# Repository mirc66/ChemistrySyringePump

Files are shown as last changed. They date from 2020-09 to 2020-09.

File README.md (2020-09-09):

# ChemistrySyringePump
arduino based 300ml syringe pump  with LED display and control buttons

Not included stepper motor or rail description

old LCD Key board Sparkfun produce 13293 now obsolete.
New LCD Key board Adafruit product 772
Uses BigEasyDriver board for stepper motor control  from Sparkfun part 12859

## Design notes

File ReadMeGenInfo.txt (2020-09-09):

ReadMe
1. final syringe pump program old board multiple selectable speeds in mL/min:syringePump300mL_revisedV2
2. final syringe pump program old board single spleed 50ml/min:syringePump300mLvs3
3. final syringe pump program New board multiple selectable speeds in mL/min:syringePump300mL_revised_NewBoardMR4_3

Orig programs received from Hans and Rob

older program:
  	SyringePump300ml.ino  
  	opening menu that says: Syringe pump v2.0
	has hardcoded single speed using the SPEED_MICROSECOND_DELAY  variable  
		SPEED_MICROSECOND_DELAY : 	a)30   for 400 mL/min ????
						b)450  for 50 mL/min
						c)2250 for 10 mL/min

Newer program:
	SyringePump300ml_revised.ino
	opening menu that says: Syringe pump
	adds variable speed control

Note:
 the pump i got from  Alex had  the old program running on it.  
Rob said the New Program should run on the old hardware

To send prog to arduino coonect straight to usb on computer not trough multi usb hub

Stepper Motor:
++++++++++++++++++++++++++++++++++++++++++++++++++++++++++++++++++++++++++++++++++++++++++++
sample code: http://www.schmalzhaus.com/EasyDriver/Examples/EasyDriverExamples.html

void setup() {                
  pinMode(8, OUTPUT);
  pinMode(9, OUTPUT);
  digitalWrite(8, LOW);
  digitalWrite(9, LOW);
}el

void loop() {
  digitalWrite(9, HIGH);
  delay(1);          
  digitalWrite(9, LOW); 
  delay(1);          
}
++++++++++++++++++++++++++++++++++++++++++++++++++++++++++++++++++++++

1.8deg/step so 200 full steps per revolution.  Big Easy Diver board defaults to 16 microsteps so total of 3200 microStep per revolution

Motor Speed:
delay() in ms since the code above uses 1ms High and 1 ms Low you each microstep takes 2ms
delayMicroseconds() in microSec eg 10microSec h ad 10 microSec low  takes 20 microSec per microStep

delay(1):	microStep/2ms*1000ms/sec = 500microStep/sec

delay(10):	microStep/20ms*1000ms/sec= 50microStep/sec

delayMicrosec(50):	microStep/100microsec*1000microsec/msec*1000msec/sec= 10,000microstep/sec

Speed:
syringe vol=300mL
syringe Barrel lenght=155mm
Thread Pitch=1.25mm  this means each ful 360 deg rev the rod avances 1.25mm
Big Easy Driver board defaults to 16 microsteps so full 360 deg rev =200step/rev*16microStep/step=3200 microstep per rev

=
300ml/155mm*1.25mm/rev*rev/3200microstep=0.000756 ml/microStep

syringeVol/syringbarrelLenght *ThredPitch/rev*rev/3200microstep= ml/microStepcalc

flow rate wanted

dealyMicrosec(50):		0.000756ml/microStep*10,000microstep/sec*60sec/min= 453 ml/min fo 50 microsec Delay
see spreadsheet Flowrate calculation syringe pump 2020	

+++++++++++++++++++++++++++++++++++++++++++++++++++++++++++++++++++++++++++++++++++++++++++++

TRIGGERING EXAMPLES:

int triggerPin=9; //not actually connected just a way to create a trigger
pinMode(triggerPin, Input);

Void set up(){}

Void Loop(){
	digitalWrite(triggePin, HIGH);
	//  other code
	if(digitalRead(triggerPin)==HIGH); {
		//do this code so the trigger Pin triggered this code
	}// end if loop
	//otherwise do this
	}//end void loop

+++++++++++++++++++++++++++++++++++++++++++++++++++++++++++++++++++++++++++++++++++++++++++++++++++
Function that returns values rather than a void function that does not return anything

Example:
int myMultiplyFunction(int x, int y){  // returns and integer(int); name of function: myMultiplyFunction; values passed: int x, int y
  int result;
  result = x * y;
  return result;// result is an integer returned to code that called the function
}

++++++++++++++++++++++++++++++++++++++++++++++++++++++++++++++++++++++++++++++++++++++++++++++

User defined Functions created in this program:
Funtion Name			void or parameter to pass
1. ckTrigger()			void
2.readSerial()			void
3.processSerial()		void
4.bolus(Direction)		pass direction( PUSH or PULL)
5.readKey()			void
6.doKeyAction(key)		Pass key
7.updateScreen()		void
8.getKey(input)			pass input
9.decToString(decNumber)	pass decNumber

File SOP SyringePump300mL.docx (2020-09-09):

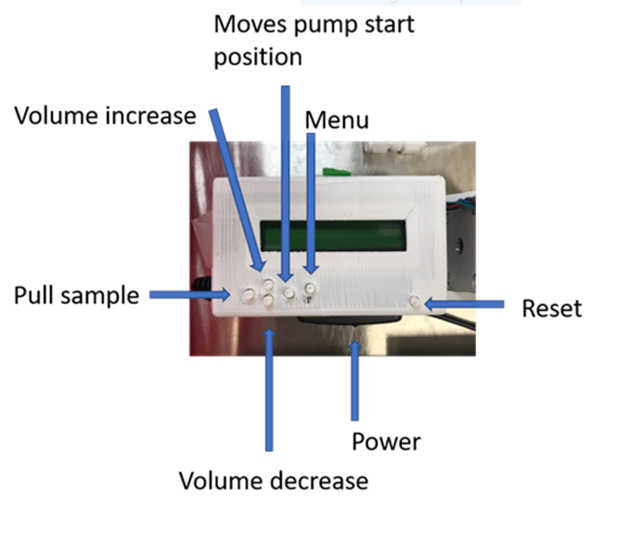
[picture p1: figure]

A-OldBoard hard coded speed of 50 mL/min

Screen at power up for older program SyringePump200mL.ino

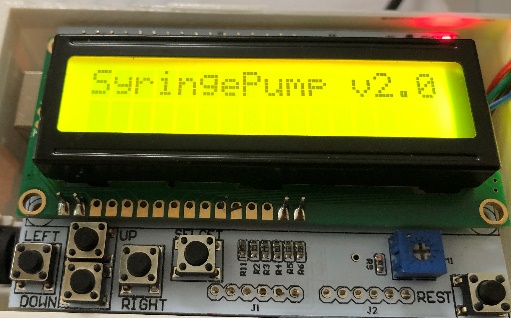
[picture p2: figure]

            1. First Time pressing Select/Menu button: This is the BolusStep Menu

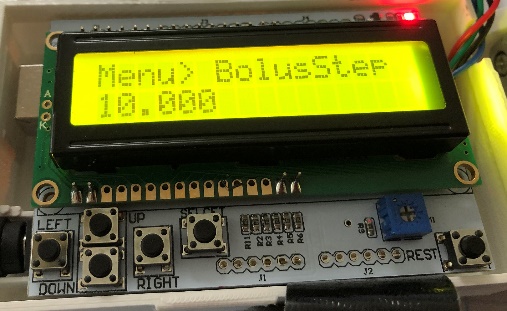
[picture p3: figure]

1. Left and right do nothing on this menu but UP or Down cycle through BolusStep options here did the down button once.

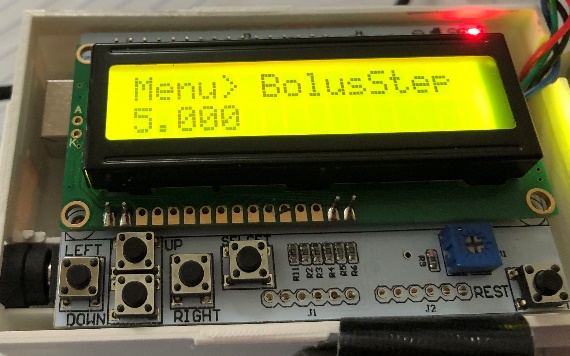
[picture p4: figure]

3.Second time push Select/Menu Button:

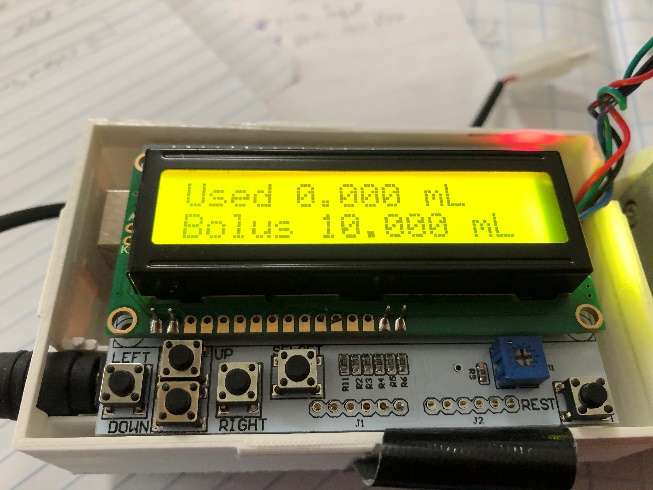
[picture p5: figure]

4. In above menu screen Left (Pull), Right (Push) from the above screen.

5.In above Menu you can change the total Bolus to sample by using up or down buttons on this screen

6. Note Used at the top of the screen will only update if used in push mode if you are pulling it remains 0.000

Old Key Pad Board can select 10 mL/min, 50mL/min or 400mL/min speeds

Open Screen Display:

1. Syringe Pump V2.0 Rob’s original code with extraneous code, old board speed =50 mL/min
2. SyringePumpV3 MR: finalized 7/14/2020 at 10:11am Maritza Romero

Same execution as v2.0 with Hard coded speed currently at 50mL/min (old board)

Old Board removed all sections of code (like triggers and Serial) that did nothing and commented code. Program hard coded speed of syringe in line below.

#define SPEED_MICROSECONDS_DELAY 450 // (450 = 50mL/min for 300mL syringe)

If you want to slow down to 10mL/min change 450 to 2250 on the above line of code

3. SyringePump (old board with selectable syringe speed included extraneous code and errors)
4. SyringePumpV4 still using old board removed extraneous code and corrected errors allows selection of syring speed onscreen

Opening screen V 4 Syringe Pump:

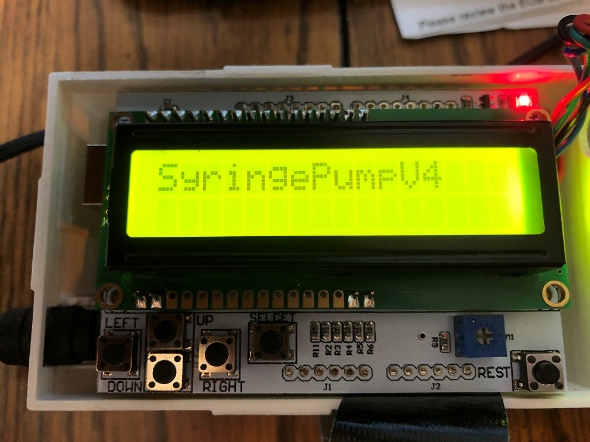
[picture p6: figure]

1. First time press menu key

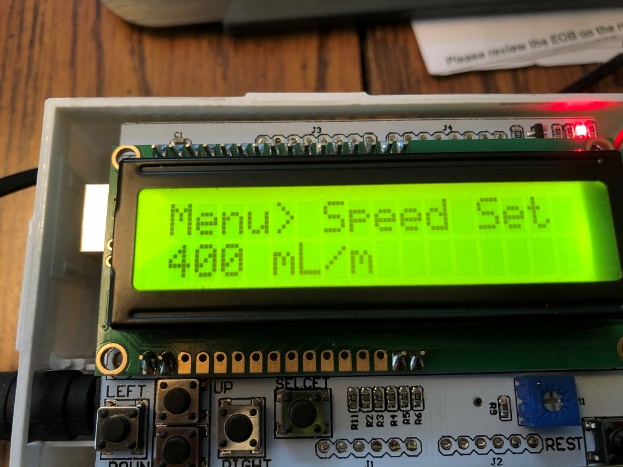
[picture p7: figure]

2. Up or down to select speed you want to use

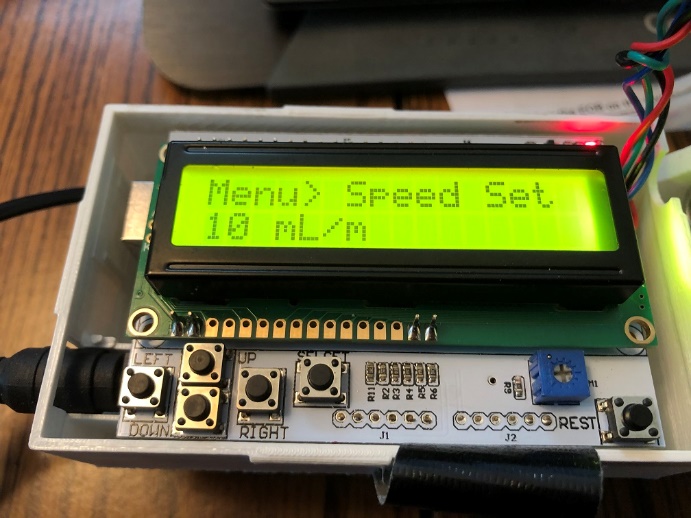
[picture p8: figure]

3. Once speed selected press the Menu button again

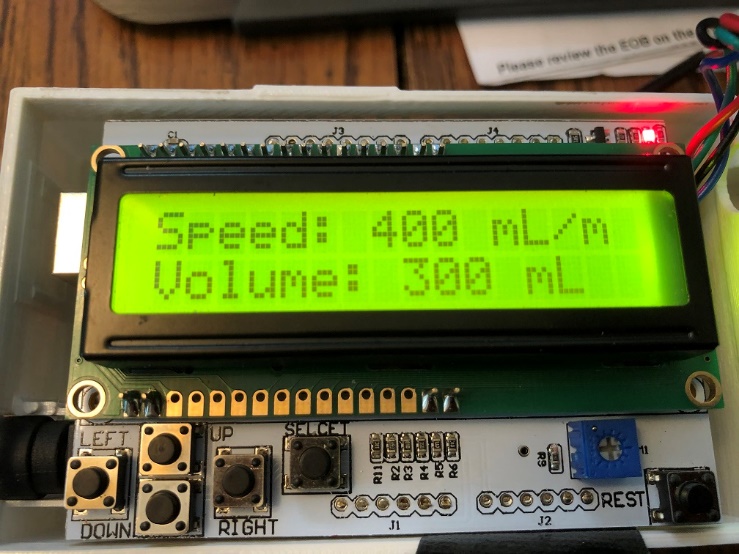
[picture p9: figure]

4. Up and down to change the volume you want to push or sample

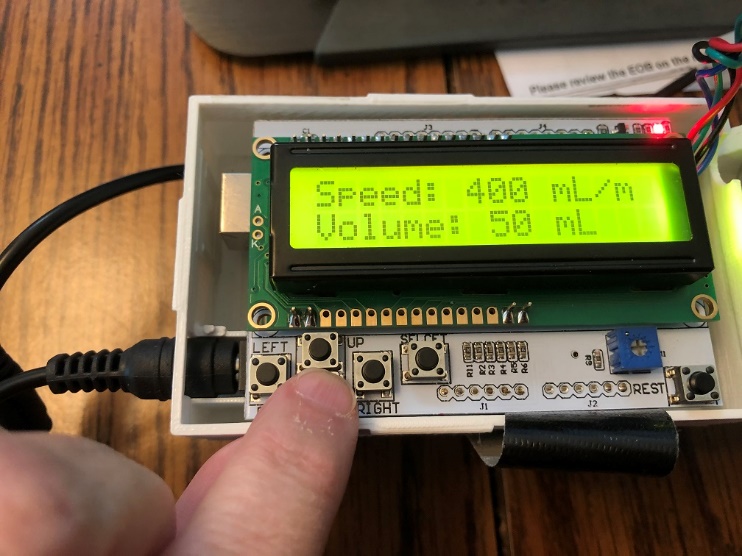
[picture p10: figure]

5. From the above screen push left to pull sample or right to push a volume

New Board : https://www.adafruit.com/product/772

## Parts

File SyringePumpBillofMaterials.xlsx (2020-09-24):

 | Part Name | Vendor | Part #: | unit | quantity | link | price with as of 9/24/2020
1 | 10Series, 1"x2"x24" Aluminum Extrusion | Amazon |  | T-slotted Extrusion | 1 | https://www.amazon.com/80-20-T-Slotted-Extrusion-Black/dp/B00IXOB7AM?s=industrial | $22.23
2 | 25PK-10 Series,Button Head Socket Cap Screw with Slide-In Standard T-Nut | Amazon |  | Screw with T nut | 1 | https://www.amazon.com/dp/B00TE30LUI/?coliid=ASIN-B00TE30LUI-ATVPDKIKX0DER&colid=2DOIGN4AECUGG | $20.89
3 | 16x2 LCD -keyboard shield | adafruit | 772 |  | 1 | https://www.adafruit.com/product/772 | $20.00
4 | arduino Uno R3 (7 to 12V with Max 20V) | Amazon |  | controller | 1 | https://www.amazon.com/dp/B008GRTSV6/?coliid=ASIN-B008GRTSV6-ATVPDKIKX0DER&colid=2DOIGN4AECUGG&psc=1 | $21.00
5 | BigEasyDriver board | sparkfun | ROB-12859 | motor driver | 1 | https://www.sparkfun.com/products/12859 | $20.00
6 | stepper motor | adafruit | 324 | stepper motor | 1 | https://www.adafruit.com/product/324 | $14.00
7 | 5 to 8 mm aluminum flex shaft | adafruit | 1176 | motor to thred rod connector | 1 | https://www.adafruit.com/product/1176 | $5.00
8 | on off switch | adafruit | 1125 | swith with barrel jacks | 1 | https://www.adafruit.com/product/1125 | $3.00
9 | Tenergy 12V 2000mAh rechargeable battery | amazon |  | rechargeable 12V battery | 1 | https://www.amazon.com/Tenergy-Capacity-Rechargeable-Replacement-Equipments/dp/B077Y9HNTF?s=electronics | $23.00
10 | Tenergy battery charger | Amazon |  | 6 to 12V recharger | 1 | https://www.amazon.com/dp/B003MXMJX8/?coliid=ASIN-B003MXMJX8-ATVPDKIKX0DER&colid=2DOIGN4AECUGG&psc=1 | $21.00
12 | connectors battery to connect to charger | amazon |  | VenomTamiya connector set | 1 | https://www.amazon.com/Tamiya-Battery-Device-150mm-Venom/dp/B000HKEVH6 | $6.00
13 | arduino to usb cable | Amazon |  | USB data sync cable arduino | 1 | https://www.amazon.com/Data-Sync-Cable-Arduino-Microcontroller/dp/B01N9IP8LF?s=electronics | $14.00
14 | 316SS- M8-1.25mm threaded rod | McMasterCarr | 94185A160 | 1 meter long | 1 | https://www.mcmaster.com/94185A160/ | $17.00
15 | Linear motion shaft | McMasterCarr | 6112K45 | Carbon Steel, 8 mm Diameter, 400 mm L | 1 | https://www.mcmaster.com/6112K45/ | $15.00
16 | Fixed alignment linear bearing | McMasterCarr | 61205K75 | for 8mm shaft | 1 | https://www.mcmaster.com/61205K75 | $20.00
17 | M3 8mm L pan head SS screws | Amazon |  |  | 1 | https://www.amazon.com/uxcell-Stainless-Steel-Phillips-Screws/dp/B012TE022K?pid=B03zHiB&s=industrial | $7.00
 |  |  |  |  |  |  | $249.12
enclosure design | https://www.thingiverse.com/thing:132497 | alt slt case

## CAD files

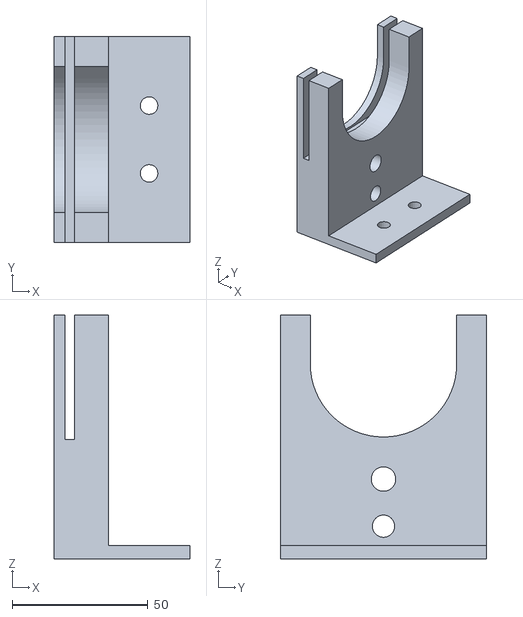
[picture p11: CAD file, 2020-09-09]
3D parts/barrel mount 300.stl
50.0 x 76.0 x 90.0

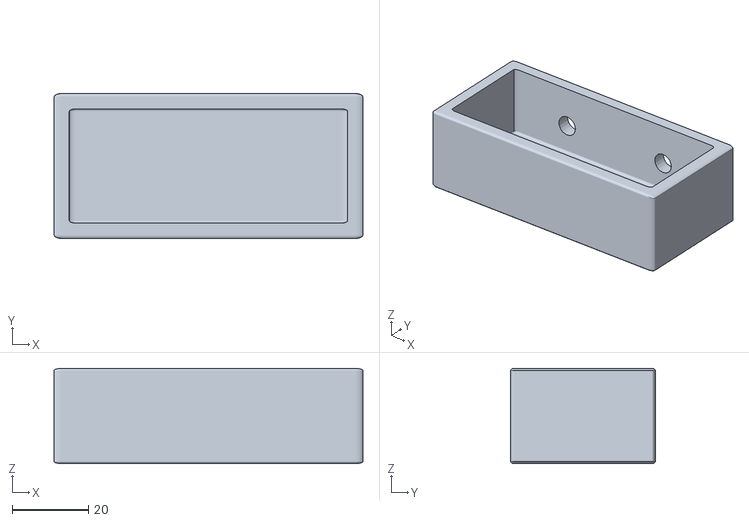
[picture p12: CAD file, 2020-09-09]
3D parts/Battery Sidecar.stl
81.0 x 38.0 x 25.0

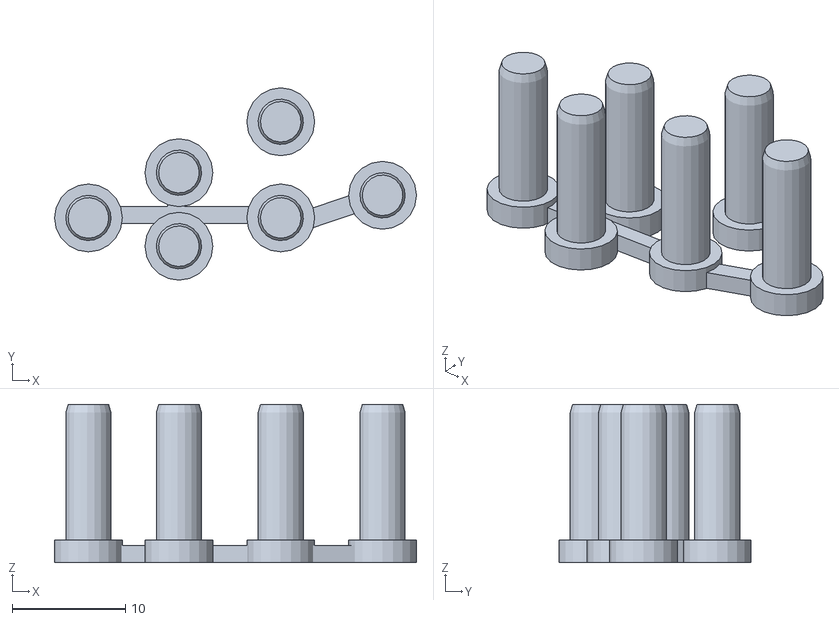
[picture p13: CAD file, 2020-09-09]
3D parts/buttons.stl
32.0 x 17.0 x 14.0

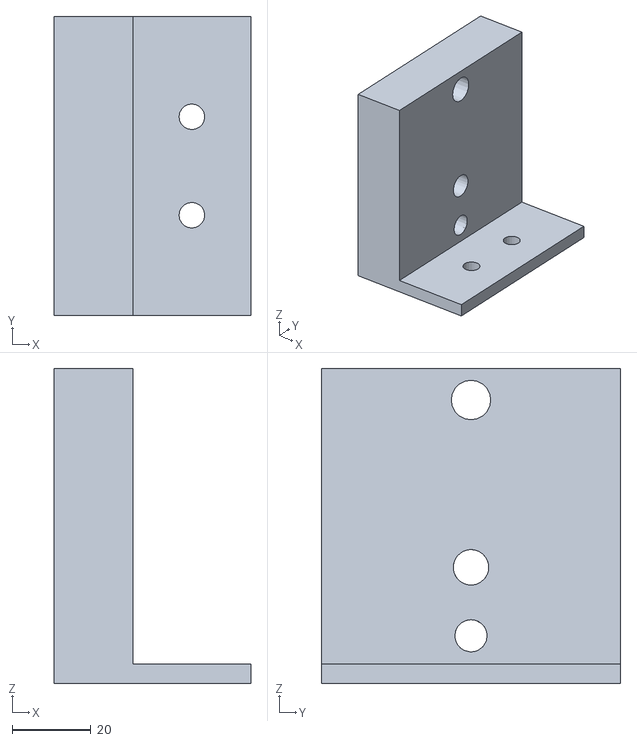
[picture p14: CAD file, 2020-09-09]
3D parts/needle mount 300.stl
50.0 x 76.0 x 80.0

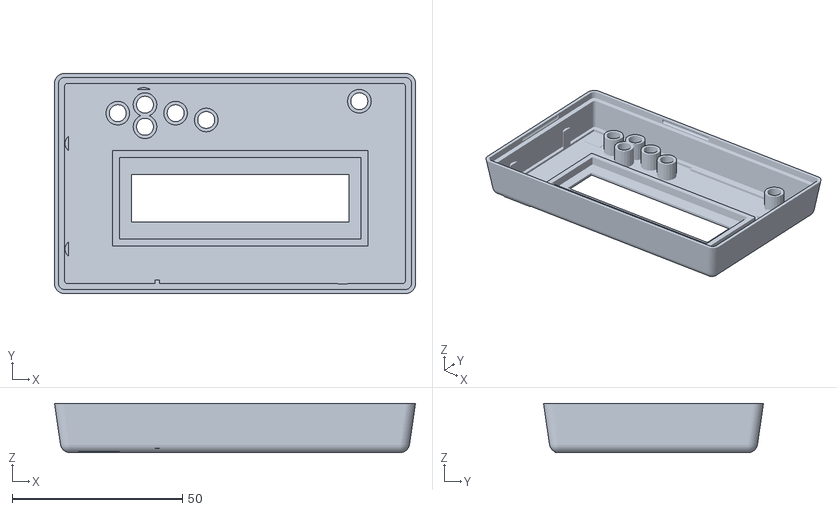
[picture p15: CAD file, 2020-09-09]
3D parts/Case top.stl
106.1 x 64.6 x 14.5

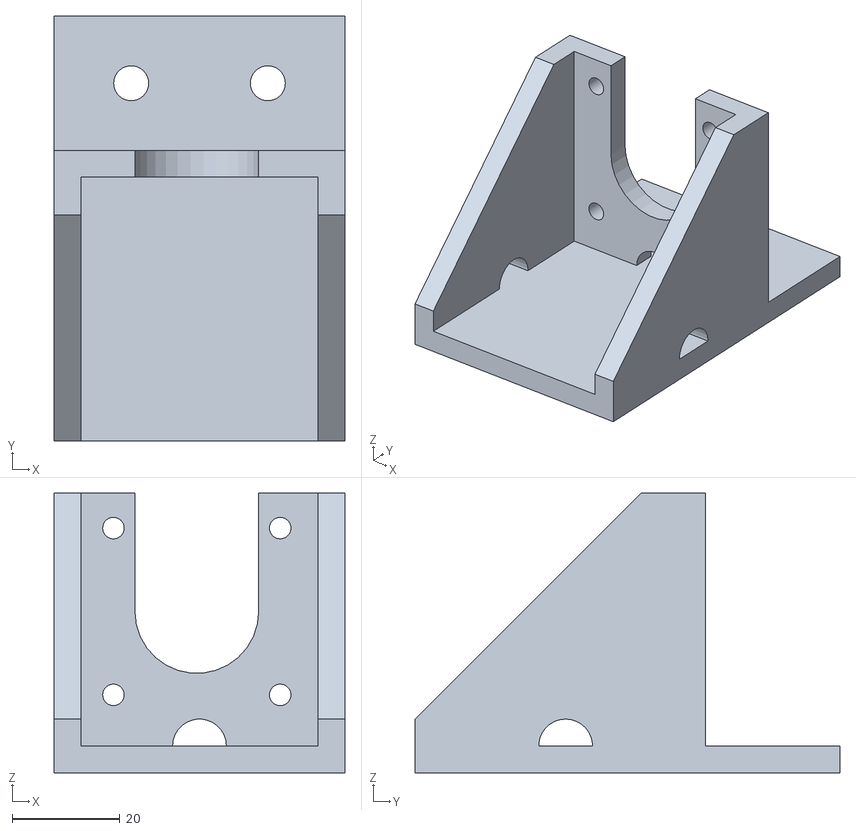
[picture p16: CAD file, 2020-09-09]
3D parts/motor mount.stl
54.0 x 79.0 x 52.0

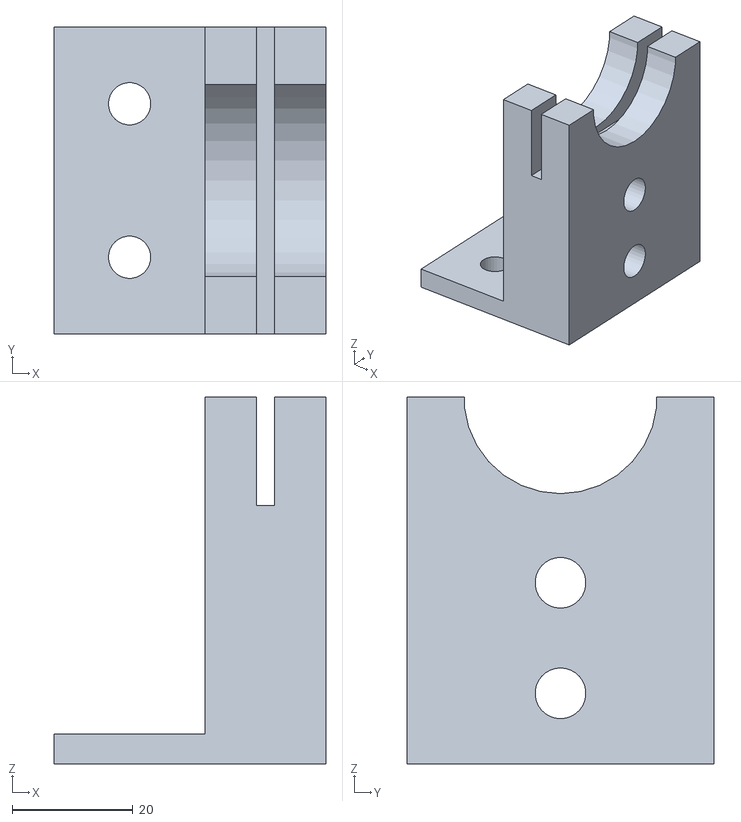
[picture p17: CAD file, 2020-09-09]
3D parts/rodMountBarrel60.stl
45.0 x 50.8 x 60.8

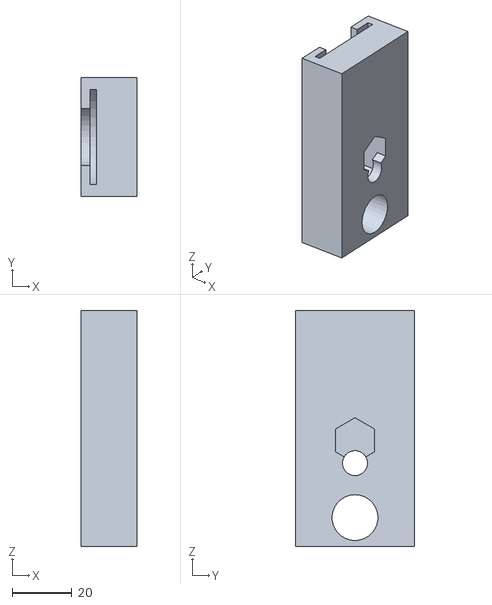
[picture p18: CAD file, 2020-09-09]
3D parts/rodMountPlunger60.stl
18.8 x 40.0 x 79.2

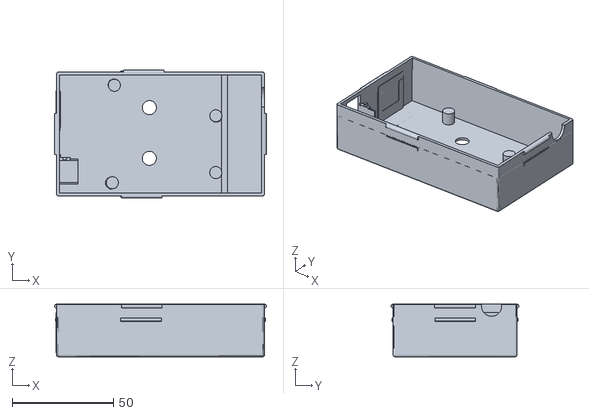
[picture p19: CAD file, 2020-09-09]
3D parts/Case bottom.stl
104.5 x 63.0 x 26.0

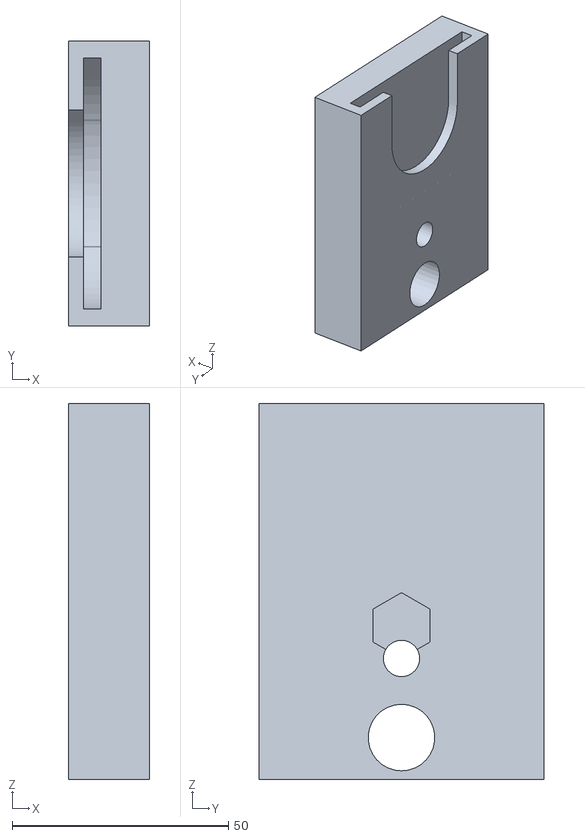
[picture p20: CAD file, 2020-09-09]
3D parts/plunger mount 300.stl
18.8 x 66.0 x 87.0

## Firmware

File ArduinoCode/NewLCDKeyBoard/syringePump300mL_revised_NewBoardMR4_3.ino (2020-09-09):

/*********************
//file:syringepump300mlrevisednewboard-MR2 ;openscreen:syringe5.2   
//      testing key recognition inside if (button&button up loop) "works"
//file:syringepump300mlrevisednewboard-MR3 ;openscreen:syringe5.3
//      testing sendind key presed to key outside the if button loop needs to use buttons variable
//file:syringepump300mlrevisednewboard-MR4 ;openscreen:syringe5.4 clean readKey()to use button
//      remove getKey()subroutine; Main Speed up and down arrows adjust speed which is set correctly
//      when you hit Select again in this menu the up and down arrows work to adjust the Volume but 
//      left and right not set up properly
//file:syringepump300mlrevisednewboard-MR4_2 ;openscreen:syringe5.4_2 works now with bolus() commented out
//file:syringepump300mlrevisednewboard-MR4_3 ;openscreen:syringe5.4_2 works now with bolus()"works"


// New Adafruit LCD-key shield https://www.adafruit.com/product/772
// BigEasyDriver board to control stepper motor:https://www.sparkfun.com/products/12859

//7/14/20 Hans asked to add 20mL/min and change 400mL/min to 300mL/min

//   SpeedSetting in microSecDelay      Speed Display in mL/min
//          2250                              10    tested with timer
//          1150                              20    tested with timer
//           450                              50   tested with timer
//            75                             300  tested with timer
//  
// The shield uses the I2C SCL and SDA pins. On classic Arduinos
// this is Analog 4 and 5 so you can't use those for analogRead() anymore
// However, you can connect other I2C sensors to the I2C bus and share
// the I2C bus.

Example code for the Adafruit RGB Character LCD Shield and Library

Note SyringePumpV5 is same as V4 but with new LCD-KEY shield board

**********************/

//=========================================== include the library code:=====================================================================================================
#include <Wire.h>
#include <Adafruit_RGBLCDShield.h>
#include <utility/Adafruit_MCP23017.h>      //port expander needed for rgblcdshield
//
//==========================================variable definitions:===========================================================================================================

Adafruit_RGBLCDShield lcd = Adafruit_RGBLCDShield();

// These #defines make it easy to set the backlight color
#define RED 0x1
#define WHITE 0x7

/* -- Constants --  placed here become global */
#define SYRINGE_VOLUME_ML 300.0
#define SYRINGE_BARREL_LENGTH_MM 155.0 //measured with ruler

#define THREADED_ROD_PITCH 1.25  //metric thread 1.25 mm between thread peaks Rod advances 1.25mm/Rev(MR)
#define STEPS_PER_REVOLUTION 200.0  //default from BigEasyDriver board
#define MICROSTEPS_PER_STEP 16.0 //big easy driver defaults to 16 microsteps per Step

#define SPEED_MICROSECONDS_DELAY 450 // (75=300mL/min for 300mL Syringe)(450 = 50mL/min for 300mL syringe) (2250 = 10mL/min for 300mL syringe)

#define mLBolusStep 10.0

float SpeedDisplay = 50.0;// in mL/min

long ustepsPerML = (MICROSTEPS_PER_STEP * STEPS_PER_REVOLUTION * SYRINGE_BARREL_LENGTH_MM) / (SYRINGE_VOLUME_ML * THREADED_ROD_PITCH );

/* -- Pin definitions -- */
int motorDirPin = 2;
int motorStepPin = 3;


//
//key#:0          1             2       3       4   //not for new board it uses the button variable
enum{KEY_SELECT, KEY_RIGHT, KEY_LEFT, KEY_DOWN, KEY_UP, KEY_NONE};//gives order of key numbers not new board
int NUM_KEYS = 5;
int adc_key_in;
int key = KEY_NONE;

/* -- Enums and constants -- */
enum{PUSH,PULL}; //syringe movement direction
enum{MAIN, SPEED_MENU}; //UI states

const int SpeedSettingsLength = 4;
//index                     0     1     2     3
float SpeedSettings[4] = {2250.0,1150.0,450.0,75.0};//in microsecDelay if this changes need to adjust updateScreen()

/*  -- Default Parameters -- */
float mLBolus = 300.00; //default bolus size in mL
int SpeedSettingsIdx = 3; //microsecDealy default array SpeedSetting begins with item idex 0 the 2250.0 microsec delay;
float SpeedSetting = SpeedSettings[SpeedSettingsIdx];// calculates to 75microsecDelay or 300mL/min

long stepperPos = 0; //in microsteps
char charBuf[16];

//menu stuff
int uiState = MAIN;
//
//===================================================================end variable definitions================================================================================



void setup() {//==========================================================void setup()========================================================================================
 
  /* LCD setup */  
  lcd.begin(16, 2);
  lcd.clear();

  lcd.print("SyrPumpV5.4_3");


  /* Motor Setup */ 
  pinMode(motorDirPin, OUTPUT);
  pinMode(motorStepPin, OUTPUT);
  
  uint8_t i=0;//uint8_t is a unsigned integer on 8 bits
}//=====================================================================end void setup()==============================================================================


void loop() {//========================================================== void loop()====================================================================================
  
   //check for LCD updates
  readKey();

    
}//====================================================================end void loop()======================================================================================
//


//=============================================================subroutines==================================================================================================
//
//fUNCT DEF TO move motor (tried placing at bottom of code caused error need to be defined before use.
//
//
 void bolus(int direction){//=======================================bolus() subroutine===
        //Move stepper. Will not return until stepper is done moving.        
  
 //change units to steps
  long steps = (mLBolus * ustepsPerML);
  if(direction == PUSH){
                digitalWrite(motorDirPin, HIGH);
                steps = mLBolus * ustepsPerML;
  }
  else if(direction == PULL){
                digitalWrite(motorDirPin, LOW);

  } 

      float usDelay = SpeedSetting;
    
      for(long i=0; i < steps; i++){ 
        digitalWrite(motorStepPin, HIGH); 
        delayMicroseconds(usDelay); 
    
        digitalWrite(motorStepPin, LOW); 
        delayMicroseconds(usDelay); 
      } 

}//====================================================================end bolus()=====
//
void doKeyAction(unsigned int key){//============================== doKeyAction()======
  
  if(key == KEY_NONE){
        return;
    }//if(key == KEY_NONE)
//==========================
  if(key == 1){//1=Select

           if(uiState == MAIN){
                  uiState = SPEED_MENU;
           }
           else if(SPEED_MENU){
                  uiState = MAIN;
          }
  }// end if (key==1)
//=============================
  if(uiState == MAIN){
//=============================read all the button    
          uint8_t buttons = lcd.readButtons();// reads all buttons
                    if (buttons) {
                             if (buttons & BUTTON_UP) {
                                       mLBolus += mLBolusStep;
                                       lcd.setBacklight(RED);
                              }//===== end if (buttons & BUTTON_UP)
                             if (buttons & BUTTON_DOWN) {
                                
                                       if((mLBolus - mLBolusStep) > 0){
                                              mLBolus -= mLBolusStep;
                                       }
                                       else{
                                              mLBolus = 0;
                                        }
                                        lcd.setBacklight(RED);
                             }//===== end if (buttons & BUTTON_DOWN) 
                             if (buttons & BUTTON_LEFT) {
                                 // for testing only
                                       lcd.clear();
                                       lcd.setCursor(0,0);
                                       lcd.print(" pull bolus ");
                                 // 
                                        bolus(PULL);
                                        lcd.setBacklight(RED);
                                 //       exit(0);// testing only stop execution so i can see message
                             }//====== end if (buttons & BUTTON_LEFT)
                             if (buttons & BUTTON_RIGHT) {
                                 // for testing only
                                        lcd.clear();
                                        lcd.setCursor(0,0);
                                        lcd.print("push bolus ");
                                 // 
                                        bolus(PUSH);
                                        lcd.setBacklight(RED);
                                  //      exit(0);// for testing only stop execution so i can see message
                             }//======  end if (buttons & BUTTON_RIGHT)
                    }//=====end if (buttons)
  }//===if(uiState == MAIN)

  else if(uiState == SPEED_MENU){
        uint8_t buttons = lcd.readButtons();// reads all buttons but define only ones needed
               if (buttons) {
                          if (buttons & BUTTON_UP) {
                                  if(SpeedSettingsIdx < SpeedSettingsLength-1){
                                          SpeedSettingsIdx++;
                                          SpeedSetting = SpeedSettings[SpeedSettingsIdx];
                                  }
                                  lcd.setBacklight(RED);
                          }//====if (buttons & BUTTON_UP)
       
                          if (buttons & BUTTON_DOWN) {
                                    if(SpeedSettingsIdx > 0){
                                             SpeedSettingsIdx -= 1;
                                             SpeedSetting = SpeedSettings[SpeedSettingsIdx];
                                    }//end if(SpeedSettingsIdx
                                    lcd.setBacklight(RED);
                          }// end button& buttondown
             
              }//end if (buttons) speed menu
  

   }//-===end else if(uiState == SPEED_MENU)
 updateScreen();//
}// end dokeyAction
//===============================================================end doKeyAction()====
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

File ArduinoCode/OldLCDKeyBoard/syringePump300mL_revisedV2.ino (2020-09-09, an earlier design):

//syringePump300mL_revisedV2 MR remove all code not used has selectable speed setting  commented Maritza Romero 7/14/2020
// Final working code for 300mL syringe with speed settings menu in mL/min for use with pumps using lcd keypad from Sparkfun

//MR this code based on Naroom Open Syringe Pump code :https://github.com/naroom/OpenSyringePump/blob/master/syringePump/syringePump.ino
//MR uses the key LCD_Button Shield VS1 board from sparkfun (obsolete now):https://www.sparkfun.com/products/retired/13293
//MR uses BigEasyDriver board to control stepper motor:https://www.sparkfun.com/products/12859

//7/14/20 Hans asked to add 20mL/min and change 400mL/min to 300mL/min

//   SpeedSetting in microSecDelay      Speed Display in mL/min
//          2250                              10    tested with timer
//          1150                              20    tested with timer
//           450                              50   tested with timer
//            75                             300  tested with timer
//  

#include <LiquidCrystal.h>
#include <LCDKeypad.h>

/* -- Constants -- */
#define SYRINGE_VOLUME_ML 300.0
#define SYRINGE_BARREL_LENGTH_MM 155.0

#define THREADED_ROD_PITCH 1.25
#define STEPS_PER_REVOLUTION 200.0
#define MICROSTEPS_PER_STEP 16.0 //big easy driver defaults to 16 microsteps not 8

#define SPEED_MICROSECONDS_DELAY 450 //longer delay = lower speed (450 = 50mL/min for 300mL syringe) (2250 = 10mL/min for 300mL syringe)

#define mLBolusStep 10.0

float SpeedDisplay = 50.0;// in mL/min

long ustepsPerML = (MICROSTEPS_PER_STEP * STEPS_PER_REVOLUTION * SYRINGE_BARREL_LENGTH_MM) / (SYRINGE_VOLUME_ML * THREADED_ROD_PITCH );

/* -- Pin definitions -- */
int motorDirPin = 2;
int motorStepPin = 3;

/* -- Keypad states -- */
int adc_key_val[5] ={622, 822, 863, 913, 940};// measured voltages at the board

enum{KEY_SELECT, KEY_RIGHT, KEY_LEFT, KEY_DOWN, KEY_UP, KEY_NONE};
int NUM_KEYS = 5;
int adc_key_in;
int key = KEY_NONE;

/* -- Enums and constants -- */
enum{PUSH,PULL}; //syringe movement direction
enum{MAIN, SPEED_MENU}; //UI states

const int SpeedSettingsLength = 4;
float SpeedSettings[4] = {2250.0,1150.0,450.0,75.0};//in microsecDelay if this changes need to adjust updateScreen()

/*  -- Default Parameters -- */
float mLBolus = 300.00; //default bolus size
int SpeedSettingsIdx = 3; //microsecDealy default array SpeedSetting begins with item idex 0 the 2250.0 microsec delay;index 1 1150.0microsecDelay; index 2  450microsecDelay
float SpeedSetting = SpeedSettings[SpeedSettingsIdx];// calculates to 450microsecDelay


long stepperPos = 0; //in microsteps
char charBuf[16];

//debounce params
long lastKeyRepeatAt = 0;
long keyRepeatDelay = 400;
long keyDebounce = 125;
int prevKey = KEY_NONE;
        
//menu stuff
int uiState = MAIN;

/* -- Initialize libraries -- */
LiquidCrystal lcd(8, 9, 4, 5, 6, 7);

void setup(){//=================================================void set up========================================================================================
  /* LCD setup */  
  lcd.begin(16, 2);
  lcd.clear();

  lcd.print("SyringePumpV4");


  /* Motor Setup */ 
  pinMode(motorDirPin, OUTPUT);
  pinMode(motorStepPin, OUTPUT);
  

}//================================================================close void set up loop (runs only once)===============================================================

void loop(){//=======================================================void loop=============================================================================================
  //check for LCD updates
  readKey();

}//=====================================================================close void loop==================================================================================
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
